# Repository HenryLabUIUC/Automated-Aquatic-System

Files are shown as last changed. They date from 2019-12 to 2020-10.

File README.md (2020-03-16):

# Automated Aquatic System
This projects includes the Arduino sketches, Fritzing diagrams, list of parts and suppliers, and various 3D printer .stl files
to build the feeding controller, and its associated peristaltic pump controller, to rear Crepidula snails and other marine
organisms. In addition, there are some dimensioned diagrams (Additional File 3) for various parts used in the automated
marine aquatic system. These files are labled and named as "Additional File #" according to the way they are referenced in
the manuscript: Henry, Lesoway and Perry, 2020, and Additional File 1, the Standard Operating Procedure (SOP) published in
BMC Biology. This project is supported by an NSF EDGE grant (no. 1827533) to J.J. Henry (J.Q.H.). See
www.life.illinois.edu/henry/tools.html

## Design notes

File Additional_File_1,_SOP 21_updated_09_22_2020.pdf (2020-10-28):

Marine Aquatic Rack System Standard Operating Procedure (SOP):

**(22 September 2020) Version 21. Henry Lab, UIUC

Jonathan J. Henry, Maryna P. Lesoway, and Kimberly J. Perry

Department of Cell & Developmental Biology University of Illinois
601 South Goodwin Ave.
Urbana, IL 61801

Note, please see the accompanying manuscript (Henry et al., 2020) and Supplemental File 2, “List of Parts and Suppliers” for more details regarding this system

This system was designed in collaboration with Iwaki Aquatics, Inc., and the automated feeding system was designed by Dr. Jonathan Henry (UIUC),
which was funded by an NSF EDGE GRANT (1827533)

Supplemental Figures are included here (called Supplemental Figures 1-4). Figure notations (to Figures 1-5) refer to those included in Henry et al. (2020). Other figure references include the corresponding Supplemental Files that accompany Henry et al. (2020), see https://github.com/HenryLabUIUC/Automated-Aquatic-System

### 1. Basic Control of the Aquatic System (Walchem Controller and Power Switches):

The main system is controlled by a Walchem 900 controller (model number WEL series 191653-20, Iwaki Aquatics, Inc., Holliston, MA; Figure 4A-B). Two electrical switches control power to the main system. A main power toggle switch (located on the bottom right of the Walchem 900 controller) will disconnect all power to the system. Note that system (e.g., main pump) power status is indicated by Alarm light A1 on the controller. A second, rotary switch (to digital input D1, on the bottom left) places the system in standby mode. In standby mode the main water pump, UV lamp, and skimmer will be turned off. In addition, the system’s electromechanical, rotary bypass valve will return to filtering mode. In standby mode all sensors will continue to operate, and the system display panel will continue to be active. Alarms may still be triggered, depending on the sensor readings. For many servicing needs, one can use the rotary standby switch to place the system in standby mode. When servicing any electrical components the system must be shut off using the main power switch and unplugged. A dedicated, 20 amp 120VAC electrical circuit is required for the operation of this system. Additional electrical circuits are needed to power other devices, such as the protein skimmer and feeding system.

Note, for specific instructions related to the use and programming of the Walchem 900 controller, readers are referred to the manufacturer’s instruction manual: https://www.walchem.com/Literature/Controllers/W900/180686_W900%20Manual_E.pdf

Some words of caution: users must be careful when accessing the system’s Walchem 900 controller to make any changes. All inputs are accepted immediately once they are entered, including any accidental changes (and no confirmation is requested when inputting changes). Any unintended changes could have a profound effect on system operation and animal welfare. At the end of this document, we include a complete list of settings used for our system.

### 2. Tools for Servicing the System (Supplemental Figure 1):

Certain basic tools are needed to service the system (Supplemental Figure 1). These include thin silicone rubber grip pads (similar to those used to open stubborn jars in the kitchen), which are handy for loosening and tightening the PVC unions. Likewise, a small filter wrench (Channellock, Inc. part no. 209, Meadville, PA) is useful for stuck PVC unions. Large and a small filter housing spanner wrenches are needed for loosening and tightening the filter bowls (Pentair parts 150296-75 and 150295-75, Pentair Aquatic Ecosystems, Apopka, FL). Two 12” standard adjustable wrenches are required for loosening and tightening various plastic pipe fittings. Basic straight and Phillips head screwdrivers for loosening and tightening clamps, etc. A specialized valve adjustment tool is needed for adjusting the tension on the large ball valves (provided by Iwaki Aquatics, Inc., Holliston, MA). In addition, an IR non-contact thermometer (e.g., EXTECH IR250, FLIR Commercial Systems, Inc., Nashua, NH) is also useful for monitoring the temperature of the main water pump housing. Handheld pH and conductivity sensors are also needed to asses water quality. The latter generally also incorporate temperature sensors as well for internal compensation. Spare fuses are needed in case the system fuse blows. Silicone grease is needed to lubricate the filter cartridge bowl O-rings. A roll of plumber’s Teflon tape is needed for sealing certain plumbing fittings. In addition, a long-handled ice scraper is useful for removing salt deposits from the system, especially those forming in less accessible areas.

### 3. The Rack Shelving Unit (Figure 1A):

The aquarium system, including the rack shelving unit was constructed by Iwaki Aquatics, Inc. (Holliston, MA). The rack is made of welded and powder-coated/painted aluminum and holds up well to salt water. Four small adjustable stainless steel feet serve to level and support the rack. As the system is very heavy once it is filled (approximately 1100 lbs/ 550 KG at capacity), these feet could eventually cause impressions in the flooring. As a precaution, and to distribute this weight, we machined a set of four ½ inch thick, 4” x 4” aluminum pads with central recesses for the leveling feet (See Figure 1A, C, and Supplemental File 3A). The typical Iwaki rack can be constructed with either five or six shelves depending on the configuration of tanks, and has a foot print of approximately 5’-6” wide x 1’-4” deep). Smaller racks with fewer shelves can also be made to order. Tall units need to be anchored either to the wall or to the ceiling to prevent them from accidentally tipping over in the event of an earthquake or if someone were to lean/pull on the unit (Figure 1A, C). There is little that needs to be done to service the shelving unit itself, other than to periodically clean it with absorbent towels and fresh water to remove spilled sea water and salts.

The main rack occupies approximately 11 sq. ft (5’-6” wide x 2” deep), which includes some space between the back side of the rack and the wall, and it is 7’-8” feet tall. For access and cleaning the rack has been placed 10 inches away from the wall. The various reservoirs, feeding system and the chiller are all external components that take up additional floor space. The feeding system (Figure 5A) occupies 3 sq. feet (1’-6” wide by 2 feet deep) and the 5 gallon sea water reservoir (a plastic bucket, see Figure 4H) requires another 1 sq. foot of space (approx. 12 inches in diameter). The external chiller occupies 1.5 sq. feet (1’ wide x 1’-6” deep). The two dosing tanks (external reservoirs) for the RODI water and a mix of calcium hydroxide, and calcium carbonate take up 1.5 and 3 sq. ft (15”x 15” and 15-½” x 21-½”, respectively, see Figure 4E).

### 4. Water Flow (Figure 2): 4.1. Water Flow During Normal Operation:

An exploded diagram has been provided to show the main parts of the aquatic system and the various routes of fluid flow (Figure 2). Note that all valves and other key components are referenced using specific numbers and initials, which we have marked with adhesive plastic labels. Relays (R#), digital inputs (D#) and alarms (A#) are numbered, accordingly, as indicated in this document. Likewise, valves are numbered for convenience, but in no particular order. Except for the needle valve #6, ball valves rotate a total of only 90° (Handle positions on ball valves relative to the long axis of the PVC pipes indicate their operation: the parallel position “|” is open; the perpendicular position “T” is closed, see examples in Figures 1L, 4N-O, Supplemental Figure 2). The ball valves typically rotate clockwise to close them and counterclockwise to open them. These directions are typically marked with arrows on the larger valve handles. Stiff, loose or leaky valves can be adjusted with a special valve adjustment tool (see below).

During normal operation the valves should be in the following positions:

1. Main pump motor inlet ball valve #4 should be completely open (Figures 1L, 2, Supplemental Figure 2A)
2. Main pump outlet ball valve #1 should be completely open (Figure 2, Supplemental Figure 2B)
3. Sensor loop ball valve #2 should be either completely open or ½ open (45° position; Figure 2, Supplemental Figure 2B)
(Note valve #2 must be completely open when using the external chiller, if it is attached to the sensor side loop.)
4. Needle valve #6 should be opened just enough to keep side bio-reactor filter loop pellets moving (Figures 2, 3L, Supplemental 2C). Turning this valve clockwise will close it. Never over-tighten this valve to completely close it, as that may damage the needle.
5. Main bypass ball valve #5 should be completely closed, unless more bypass water is required to return to the sump to prevent cavitation or to limit water flow to the tanks (Figures 2, 4N-O, Supplemental Figure 2D, see below).
6. Ball Valve #7 (“AT”) should be completely closed (Figure 2, Supplemental Figure 2E; this is the Accessory Tap Filler valve for the attached blue hose, see below).
7. Spring loaded “quick connect” drain valve #3 should be closed (Figures 2, 3L, Supplemental Figure 2C, e.g., with nothing attached!) This is the main drain valve. This male valve automatically opens when the female connector is attached, see below.
8. Individual ball valves to each row of tanks (rows lettered A-F, from top to bottom) should be adjusted as needed: typically, ½ open (45° position). If there are no tanks on these rows they should be closed (Figure 2, Supplemental Figure 2F).
9. Individual tank ball valves should be opened as needed (Figures 1D, 2, Supplemental Figure 2G). Typically, these should be completely closed if there are no tanks or open fully or less, as needed. Typically, these are set to ½ open (45°) for the 3 l tanks and both are set completely open for each of the 10 l tanks.

### 4.2. Water Flow During Feeding

(Electromechanical bypass valve, input from R3, regulated by D5; Figures 2, 5I, Supplemental Figure 2H):
Note that during feeding the filter loops (including the bioreactor side loop; Figure 2 and 3K) will be bypassed so that food can freely recirculate between the sump and the tanks. This is achieved by a motorized ball valve (Figures 2, 5I, Supplemental Figure 2H). The bypass valve is regulated by relay R3. When the relay is open, the system is in filtering mode. When the relay is closed, the system is in feeding mode. Normally, the state of relay R3 is controlled by a digital input from the feeding system (D5). A small window on the bypass valve “BP” indicates its current status (Supplemental Figure 2H). If the window is black, the unit is in filtering mode. If the window is white (side of stem colored with white paint), the unit is in feeding mode. When the valve is in the feeding position, Alarm light A3 will be illuminated. During the feeding mode, sea water will not pass through the filters due to the presence of a reverse flow check valve (Figures 2, 3L). Water flow will thus encounter less resistance due to the removal of the filters and no water will return to the sump via the small bioreactor filter loop. Therefore, during feedings the effluent, outlet pressure indicated on the round gauge will rise approximately 3psi (e.g., with a new pleated filter from approx. 10-13 PSI to 13-16 PSI; Figure 2, Supplemental Figure 2B). The flow rate to the tanks will also increase somewhat during feeding from by approximately 3 lpm (e.g., with a new pleated filter from 29-30 l/min to about 32-33 l/min, or possibly as high as 34l/min). (Note that the level of water in the sump will be lowered by about 0.5 to 1 cm during feeding). The noise level of water flowing through the main pump will generally increase during feeding. This is normal, but one should pay attention for any signs of cavitation (see below). The only bypass water that will return to the sump during feeding will come back via the sensor loop, unless the main bypass loop (valve #5, Figures 2, 4N-O, Supplemental Figure 2D) has been opened somewhat. Note that depending on the flow rate, some bypass water must return back to the sump or cavitation may occur (see below). The UV lamp will continue to operate during feeding, as it requires flowing sea water to cool it (otherwise the PVC housing would melt!; Figure 3I). During feeding the skimmer is also turned off (Figures 3C-F, 5G-H). When the filters are turned back on after feeding, there may be a slight delay in the formation of new skimmate by the protein skimmer (though we have not yet encountered any such problems). There is normally no need to make any system adjustments during feeding.

Note that as the filters become clogged, the effluent outlet water pressure will drop (as will the overall flow rate). Pressure on the intake side of the filters will increase while that on the outflow side will decrease (the latter being the pressure read by the small round gauge; Figure 2, Supplemental Figure 2B). This gauge can be used as an indicator for potential problems or when it is time to replace the pleated 50µm filter (Figure 3G, Supplemental Figure 2B), though the reading is somewhat misleading. For instance, if one opens up the valves supplying the small tanks this pressure reading will drop and the flow rate will increase. Typically, filter replacement is required when the inlet and outlet pressure difference is 10psi. Once the pressure difference gets above that, there is a small risk that the filter cartridge can collapse/crush. In our system there is no second gauge that reads inlet water pressure to the filters, so the pressure difference cannot be determined. Most labs care more about the flow rate to the tanks than the pressure in the filters. There is a direct relationship between flow and pressure with pumps, so it's easier to just change the filter according to changes in flow rate. As the filters become clogged you will also notice that the noise level of the system will become quieter, as less splashing water returns to the sump. It is recommended to change the filter once the system's filtered flow rate drops to no lower than 20 lpm, but one can change the filter before that point. One can gain some additional time before needing to perform a filter change by simply opening up the valves that supply sea water to the manifolds for each row of tanks (valves A-F). This will also impact the flow occurring during feedings, which will also be elevated (one should limit the maximum flow during feeding to around 35-36 lpm). At some point though, the effluent water pressure will drop to low and the float switch will not rise, triggering a no-flow alarm. At that point the filter must be changed immediately, as this will begin to impact the reading of temperature, conductivity and pH, which may lead to lethal changes, as the system tries to compensate for the false readings! While in some other applications it may be possible to clean clogged filters, in our case the biofilm, finer debris and algae trapped by the filter material are much harder to remove simply by washing the filter, and, thus, the filters must be replaced. Furthermore, the material that is trapped by the filter will continue to break down within the system, so the longer the waste/food stays in the system, the more organics/nitrogenous waste will accumulate in the water. Filtering flow rates with new filters are around 29-30 lpm, and effluent pressures should return to around 10-12psi (32-34 LPM and 13-15psi during feeding). We have observed approximately two—three months of service life for each pleated filter.

### 5. Individual Tanks (Figures 1D, 2):

The polycarbonate tanks are manufactured by Pentair Aquatic Ecosystems (Apopka, FL; Figure 1D-G). These tanks accept slotted or nylon mesh “larval” baffles (Figure 1F). The larval baffles are available in three mesh sizes (400, 700 and 1000µm). These baffles slide into molded channels in the back of each tank and are fairly secure. Their purpose is to prevent animals from reaching the rear drain tube where they could travel to other parts of the system. In this system we use baffles with 400µm openings, which are small enough to prevent Crepidula atrasolea embryos or juvenile snails from escaping the tanks. Each tank is equipped with a plastic lid (Figure 1E). Unused holes in these lids are plugged with small white plastic snap caps to help limit evaporation and water spray (Figure 1G; McMaster Carr, part number 9688K25162PP050BG14, Elmhurst, IL). These plugs can be further sealed using silicone aquarium cement (Supplemental Figure 2G).

1. NOTE: When servicing a tank, first shut off the tank’s own valve(s)! Then remove the white tubing from the lid access hole(s) before removing the lid or the tank. Be aware that there may be a lot of moisture (typically fresh water condensate) under the lids. When removing a lid, be careful to drain this condensation back into the tank to prevent a mess.
2. If the tank is to be removed, tilt the tank backwards to drain off some sea water first. Remove the tank carefully so as not to spill the sea water. Lift the tanks straight up to clear the drain tube from the drain cover (Figure 1H-J), and the ridges on the bottom of the tank, which straddle the rack cross bars (Figure 1E, G). When done, reinstall tank and/or lid in reverse order, insert the tubing and then turn the tank valve(s) back on. It’s easy to forget this last step. Remember to seat the tanks properly, as they have protruding plastic ridges on the bottom that must seat properly onto the metal rack cross bars (Figure 1A-D).

One can operate the system with any number of tanks in service. However, when taking tanks on or off line, they should be added or removed with sea water in them. Otherwise, the sea water level in the sump will change.

The mesh on the larval baffles will eventually accumulate a biofilm and waste products, which will impede the flow of drain water. This could lead to an overflowing of sea water from the tank, which could eventually drain the sump. These larval baffles must be cleaned periodically, and it is best to do this on a predefined schedule (every month or two).

Note that if the flow of water through any of the small valves that serve individual tanks becomes reduced, this may be an indication that they have become clogged. Opening and closing the valve may correct the problem, or one can try to unclog these valves by temporarily shutting off all the rest of the small valves that serve other tanks on that particular shelf. The greater force of the higher water pressure will usually dislodge any debris and restore normal water flow thru the clogged valve. If this does not correct the problem, it will be necessary to remove (unscrew) the valve from the manifold to manually clean or replace it.

### 6. RO and pH Reservoirs (Figures 1A, 2, 4E):

(pH pump currently not in use)
Two plastic reservoirs with lids hold RO (RODI) water and a concentrated salt solution, respectively (Figures 1A, 2, 4E). Be sure to periodically check the levels and refill the RO (dH2O) water and pH salt reservoirs, as needed. Make sure the reservoir lids are correctly installed and the filler intake/vent tubes are in place! The filler tube has a cylindrical weight to keep it submerged. For the pH reservoir one can mix dH2O with Na-bicarbonate (dissolved to about one half of its saturation point, or 40gm/liter) and Kalkwasser (Ca-hydroxide, dissolved to about half its saturation point, Bulk Reef Supply, Golden Valley, MN). Note, however, that we have not been using the pH pump, and have inactivated this by placing it in HOA off mode (see additional note, below). Rather, we adjust pH manually, as needed. On rare occasions, during the initial establishment of this system, the pH dropped by 0.1 unit. To correct this we added 5gm of Marine Buffer (Seachem, Madison, GA) per 40 gallons of sea water. This elevated the pH by 0.1 unit. More recently, we saw a slight elevation of pH. To correct this issue, we performed a series of partial water changes and began to supplement ionic calcium (see Section 11: Monitoring Water Quality, and Section 45: Elevated pH, below).

### 7. Adjustment and Priming of the RO (input from R4) and pH (input from R5) Pumps (Figures

2, 4F):
RO and pH pump operation are indicated by Alarm lights A4 and A5, respectively. Normally, these small red and blue electromagnetic relay pumps, mounted on the back wall to the right side of our rack system, make a distinct rhythmic sound during pumping (Figure 4F). When the pumps are running dry and pumping air they will make a much louder popping sound. This is not good for the pumps and is caused by fluid level in the reservoirs being located below the weighted inlets of the supply/vent tubing, or the pump(s) may need to be re-primed. Priming is accomplished by opening the small round plastic valves on the very top of the pumps (Figure 4F, see the manufacturer’s instruction manual). Make sure there is enough liquid in the reservoirs. Allow the pumps to run by placing them in HOA “On” mode using the main system control panel. The pumps are primed when fluid starts to exit the vent tubes that hang back down into the reservoirs. At this point the small valves should be closed to allow the fluid to pump to the sump instead. Be sure to verify that this is working! After the problem is corrected return the pump control to HOA “Auto” mode using the main system control panel. RO pumping rate is set to 40 pulses per min. This must be set on the front panel of the RO and pH pumps themselves (Figure 4F; follow the manufacturer’s instructions, Iwaki Co. Ltd., Holliston, MA). Adjustments can only be made in the upward direction, so if you miss your desired setting you must go all the way up and back to zero to reset the proper value. These values are typically set to be “locked” on the RO and pH pump control faces so that one cannot accidentally change these (users are referred to the pump manufacturer’s manual for full operation). Pumping rates may be changed, if needed. For example, if the restored levels tend overshoot those desired, then the pumping rate can be lowered (e.g., conductivity overshoots and goes too low, triggering an alarm, during RO water pumping). With lower pumping rates the pump will tend to run longer but the water will have a better chance of mixing so values will be able to stabilize , which helps limit false readings made by the sensors.

**So far, we have not seen any need for the pH dosing pump. pH levels appear to be holding fairly steady; though earlier we had noticed these values slowly drop once we added animals and began to feed them, and more recently (after eight months of operation) we saw a slight elevation in pH (see Section 11: Monitoring Water Quality). We are considering a change to the use the pH pump to deliver periodic, scheduled doses of Ca++ to the system to enhance shell growth.

### 8. Servicing the Sump Pad Filter (Figures 2, 3A):

The sump has a coarse, fibrous polyester filter pad that sits on a perforated sieve plate (Figure 3A). Dirty sump pad filters may be carefully removed allowing any sea water to drain back into the sump and replaced with a fresh filter, as needed. To accomplish this, one must remove the Tent or Origami cover (Figure 3B, Supplemental Figure 3A-C). It is not necessary to remove the slotted PVC drain diverter or to shut the system down to change the filter pad. Change the filter when it becomes discolored and sea water starts to spill over the edges rather than pass thru the filter material. These disposable filter pads should last a few months.

### 9. Servicing the Protein Skimmer (regulated by D5, input from R7, Figure 3C):

The sump contains a compact Tunze protein skimmer (Tunze Comline DOC Skimmer, 9004 DC, Penzberg, Germany) that fits inside the left compartment of the sump on the far left side (Figures 2, 3C-F). Protein skimmer status is indicated by Alarm light A7. It is illuminated whenever the skimmer is turned off, which occurs during a feeding cycle. The protein skimmer is located in the sump and runs automatically when the filters are active, but is turned off during feeding via a custom microcontroller circuit (Figure 5G-H; see Supplemental Files 15-18). Normally, a low level output (0) from pin 3 of the Tunze motor controller’s ATMEL 1724 microcontroller turns on the 12 volt DC motor, and a high level output (1) stops the motor. This is the output that is being intercepted by the accessory microcontroller interface, under control of a signal sent by the Walchem 900 controller, when it receives the over-riding command from the feeding station’s microcontroller. In other words, when it is time for feeding, the feeding station sends a signal to the Walchem 900 controller to activate the bypass valve (see below). The Walchem 900 controller then sends a signal to the accessory skimmer control circuit which, in turn, interrupts the output of the DC motor controller’s own microcontroller to turn off the skimmer. Note that the blue skimmer control power light (located inside the skimmer control box knob) will stay illuminated even during feeding (Figure 5G). One can override skimmer function and turn off the skimmer at any time for a preset period (approx. 10 mins) by pushing the small button on the small skimmer control box (Figure 5G, the blue light will then go off). The skimmer can be turned back on by pushing the button again or it will automatically turn on after the preset time interval. The speed of the skimmer DC motor is regulated by the illuminated knob on the control box (Figure 5G). Typically, this only needs to be set to the 30-50% position, as needed. If this is adjusted too high, excess sea water will enter the skimmer cup. If this is set too low, no skimmate will be formed. This needs to be adjusted empirically. Skimmate needs to be removed from the collection cup (Figure 3D-G), and its rate of formation depends on several factors, including the size and amount of bubbles and the concentration of dissolved organics. As supplied, the removable Tunze skimmer collecting cup does not have a drain tube. We have installed a silicone drain tube that exits the sump on the left side through a bulkhead compression fitting located just above the high water line on the far left side of the sump (Figure 3D, F; silicone tubing: 0.188” ID x 0.375” OD, Dow Corning, Midland, MI). Be careful with the skimmer’s silicone drain tube. If it becomes disconnected from the small collecting cup the skimmate will simply flow back into the sump. If it gets kinked and collapses inside the sump bulkhead connector, a leak may form. This tubing can be fed to an external tray to collect the skimmate (Figure 3G). Note, however, that sea water can enter the collecting cup, as described above (and also see note below), and this would drain out of the tubing to the bucket. A great deal of water could flow through this tubing, which is located just at or slightly below the high-water level in the sump! This could create a huge mess, though we have never encountered such a problem. Alternatively, the open end of the tubing can be elevated well above the water level in the sump and lowered to drain the skimmer cup, as needed. Periodically (once every week or so) one should wipe clean the inside of the skimmer collection cup, its airlift (chimney) and the lid, which will accumulate a great deal of algae and other proteins. More skimmate will form if one keeps the chimney clean (Figure 3E). The skimmer is normally controlled by relay (R7). When relay R7 output is low/off (0) the skimmer will run and when relay R7 is high/on (1) the skimmer will stop.

Note that the skimmer is held in place by two strong rare earth magnets (Figure 3D) enclosed within the blue and black plastic disks located on the outside, left side of the sump. Do not remove these magnets or attempt to reposition the skimmer. (Also, never put the two magnets together as you will not be able to separate them without tremendous difficulty!). The skimmer sits on top of a perforated platform inside the sump. The platform has four leveling, height adjustable legs. These are set so that the slotted openings in the skimmer cup are located just along the sump high water level (Figure 3C). Sea water must be able to enter these slots. The relative water level in the sump is critical for proper function of the skimmer. It should be about halfway up between the top and bottom edges of the intake slots located within the skimmer cup. If the water level is too low, or the skimmer is placed too high, no skimmate will form. If the water level is too high, or the skimmer is placed to low, the skimmer will pump excess water into the collection cup and its drain tube. Precise sump water level is maintained by the RODI pump and the ATO units (see Section 6: RO and pH Reservoirs, above, and Section 33: Automatic sea water Top-Off system (ATO), below). Note that skimmer activity and the Walchem 900 front panel alarm light A7 are regulated by the input from the feeding system (to D5).

Note that the fine bubbles produced by the protein skimmer can also produce jet drops and a fine mist that collects under the lid and this moisture drips into the collection cup. This can fill the cup prematurely, and removes some “clean” system sea water. Careful adjustment of the DC motor’s speed can help limit this mist and any lost sea water. Approximately 25-100 ml of liquid waste will be collected by the skimmer each day.

Note also that if you perform a partial sea water change, you may see some excess water being ejected into the skimmer cup, which may flood the collecting tray. This can continue for a couple of days, and it is best to monitor this. It is unclear why this happens, as the level of sea water in the sump is not changed. One can simply turn down the skimmer settings, or elevate the skimmer drain tube to prevent the loss of sea water from the system while this is taking place.

### 10. Servicing the Cartridge Filters, General Instructions (Figures 2, 3G, K) :

The system has four cartridge filters (see Figure 2): 1) a 50µm pleated filter (Figure 3G, Supplemental Figure 3D), 2) a biological filter (Figure 3G), 3) an activated carbon filter (Figure 3G), and 4) a small nitrate bio-pellet reactor (Figure 3K).

1. When servicing the cartridge filters, put the system in standby mode, or shut off the system. The main pump must be shut off. Wait for about one minute for all the sea water to drain back to the sump, once the system is placed in standby. Service each filter, one at a time, as needed.
2. Close valves #4, 1, 2, 6 and 5.
3. Drain sea water using valve #3 with a push-on, female quick connector and its short piece of tubing. (Use a large clean beaker to collect the sea water, which will be returned to the system.)
4. Also purge some air and additional sea water (via valve #3) from each filter by pushing the purge valves on the top back sides of the filter housings (Supplemental Figure 3E).
5. Remove the stretchy nylon opaque sleeve, and use filter wrenches to loosen the filter bowl over a 3-5 gallon bucket to catch the sea water (Supplemental Figure 3D-F).
6. Once loosened, use both hands to completely remove the filter bowls with their contents. Note that the filter bowls are full of sea water and media, and are very heavy. Do not let them fall and crack.
7. Be sure to reassemble filters correctly with the appropriate cartridges, gaskets, etc. and in the correct orientations. A little 95% pure (Danco #88693, Irving, TX) silicone grease may be used on the filter bowl O-rings and threads.
8. Filter bowls should only be tightened by hand. You may use the filter wrenches only sparingly. Do not overtighten the filter bowls, you can crack the plastic or seize the threads!
9. Return the valves back to their original open states.
10. Turn the system back on.
11. Return the collected, drained sea water back to the sump. As you will tend to lose some sea water, the sump level will be low and you will likely need to add additional sea water to the system to return the level back to normal. This can be done by simply turning on the ATO unit briefly, see Section 33: Automatic sea water Top-Off system (ATO), below.

### 10.1. Servicing the Pleated Mechanical Filter (Figures 2, 3G):

The 50µm pleated filter (Supplemental Figure 3D; GPE50 Keystone Giant Filter Cartridges, CECO, Telford, PA) should be changed when it becomes discolored and begins to impede sea water flow (reducing the flow rate to nearly 20 lpm, see above). These polyester filters are easy to install and have no polarity. The pleated filters typically have a life span of a few months. Note that when the pleated filter is changed, the system’s effluent pressure and flow rate should rise. The increased flow rate will tend to drop the water level in the sump, somewhat. Therefore, some additional sea water may need to be added to the system to raise the water to its nominal level. The automatic top off unit (ATK) would also raise this level the next time (day) this unit will run. It is recommended to cover the filter bowl with dark, opaque material to discourage algal growth on this filter (Figure 3H).

### 10.2. Servicing the Biological Filter (Figures 2, 3G):

The main biological filter consists of a mix of 800 gm of Matrix (Seachem, Madison, GA) and 100 gm of de*Nitrate (Seachem, Madison, GA, see Figure 3G). This highly porous media serves as a substrate for aerobic and anerobic bacteria to process ammonia, nitrite and nitrate. This quantity of media has over 1400 sq. meters of surface area to support bacterial growth. The inclusion of some de*Nitrate granules in the biofilter also helps to remove nitrates. Note that there is a small 3” diameter sponge-like filter inside the biological filter canister to help retain the pellets. The biological filter media should never need to be replaced. Typically this filter requires no servicing; however, it can be rinsed while still inside the cartridge using clean sea water and a 5 gallon bucket, if needed, to remove any debris. Never rinse this filter with fresh water as this would harm the bacteria! It is recommended to cover the filter bowl with dark, opaque material to discourage algal growth on the filter (Figure 3H).

### 10.3. Servicing the Activated Carbon Filter (Figures 2, 3G):

The activated carbon filter contains approximately 1-2 lbs of activated carbon pellets (Figure 3G; Kent Reef Carbon Pellets, Kent Marine, Franklin, WI). Activated carbon is a porous substance with a very high capacity for absorbing organic materials. The carbon pellets can also serve as a substrate for nitrifying bacteria. The activated carbon (Kent Reef Carbon, Kent Marine, Franklin, WI) should be replaced, as needed. This filter cartridge holds a considerable amount of activated carbon (about two pounds) and should last for a year or more. This is far more carbon than is needed and some recommend using far less or even no carbon at all. Unfortunately, there is no good way to tell when this filter is depleted. If the sea water should turn yellow, it might be time to change the activated carbon. Note that there is a small 3” diameter sponge-like filter inside the activated carbon canister to help retain the pellets, and this should be rinsed and reused if the media is changed. We recommend changing the activated carbon every one to three years. Only half of the carbon should be changed. When replacing the activated carbon, one needs to thoroughly rinse the new carbon in dH2O to remove fine particulates. A mesh bag is provided for this purpose; however, one can also rinse the carbon directly in the cartridge using a large plastic bucket (only if all the carbon is being changed). One concern is that the activated carbon may impact the pH of the system. This issue seems to depend on the source of the carbon. One should monitor this carefully. Activated carbon may also remove certain trace elements from the sea water. Commercial preparations may be used to add back trace elements. If used, they should be added when the filters are in bypass (feeding) mode. Activated carbon may also release phosphates into the sea water, which is not desired. The activated carbon also acts as an additional biological filter, providing substrate for bacteria. One should cover the filter bowl with dark, opaque material to discourage algal growth on the filter (Figure 3G).

### 10.4. Servicing the Nitrate Bio-Reactor (Figures 2, 3K):

A small bio-reactor side loop filter (nitrate bio-reactor) has been included to encourage the growth of denitrifying bacteria (e.g., both aerobes and anaerobes, etc.) to help remove nitrogen (nitrates; see Figure 3K). A relatively small amount of water is slowly diverted to this side loop via the needle valve (#6; Figures 2, 3L, Supplemental Figure 2C). Needle valve #6 should be opened enough to keep side filter loop PHA pellets moving gently. (Turning this valve clockwise will close it). Never over-tighten this valve as that may damage the needle. The PHA pellets (Vertex Aquaristik Pro-Bio Pellets, Huntington Beach, CA) must be kept moving to dislodge the accumulating bacterial byproducts in which the nitrogen is being sequestered, and to prevent the pellets from sticking together. These PHA pellets contain a source of carbon needed by the bacteria to remove the nitrates. It is best to keep the bio-reactor in a dark area away from light to prevent algal growth (we cover this canister with dark, opaque material). These nitrogen rich by-products need to be removed from the water using the protein skimmer. Ideally, the water from the side loop should be returned directly back to the sump, near to the protein skimmer’s intake. To service the bio-reactor, place the system into standby mode or shut off the flow of water to the side loop (close valve #6).

If the flow of water is too slow or if a large amount of bacterial film and their by-products begin to accumulate, the pellets my stick together and stop moving. One can place a small 1/2” long yellow Teflon coated magnet (i.e., stir bar) inside the bio-reactor filter cartridge along with the PHA pellets. One can then use another strong rare-earth magnet, which is held externally by the hand, to move this stir bar and dislodge any stuck pellets without having to shut off water flow or open the filter. Alternatively, if the pellets refuse to move one should open the filter. To accomplish this, shut off water flow to the side reactor (Valve #6), bleed in some air by pushing the purge valve located on top of the filter holder, and then remove the filter bowl. As long as valve #6 is fully closed, it should not be necessary to shut off the main pump, or place the system into standby mode, to perform this service (One should verify that no water is returning back to the sump via the return hose connected to this filter, though it is perhaps safer to place the system in standby mode). Note that if the pump is running, some signs of cavitation may be detected. In that case, simply open up the main bypass loop just a little bit until cavitation stops (Valve #5). Note that the bio-reactor is located in a rather confined space next to the main pump, so be careful not to spill sea water when removing the cartridge bowl. Once the bowl has been unscrewed, it must be tilted to remove it; therefore, some water should first be removed using a large pipette to prevent spilling. Be careful, the main pump motor with its electrical connection is located adjacent to the bioreactor! Once enough water has been removed you can carefully tilt and lift out the filter bowl without spilling the remaining sea water. (By following this procedure, one should not have to remove the carbon filter to remove the bioreactor filter.) Once the bowl is removed, you will notice that the inner cartridge has a round cap and a slotted filter screen to prevent debris and pellets from leaving the filter, and these must be cleaned. Make note of their correct orientation for proper reassembly. Pull out the cartridge slowly and then slowly poor off some sea water remaining in the bowl and save this. The cartridge can then be placed back in the bowl, and vigorously moved repeatedly up and down inside the sea water remaining in the filter bowl to dislodge the bacterial film. One can also use the long plastic pipette to vigorously stir the pellets. Remove the inner cartridge from the bowl with the pellets and discard the dirty sea water left in the filter bowl. Repeat this wash one more time with some more of the clean sea water. Only clean the little round slotted screen in the sink using distilled water and wipe clean using paper towels. Do not rinse the cartridge, bowl or pellets with anything other than sea water, so as not to destroy the bacteria! Reassemble the various part of the filter in the reverse order and screw the bowl back in place. Once the filter is replaced, restore water flow to the bio-reactor side loop (open valve #6 just enough to get the pellets moving). If they are not cleaned sufficiently, fragments of biofilm may continue to come off the pellets and be drawn into the slotted plastic filter screen, which could impede water flow, and this would need to be re-cleaned. Note, to get all the flowing sea water back into the bio-reactor’s filter bowl, the purge valve needs to be pressed to remove the air (you may hear a little hiss as the air escapes). Stop pressing this button once all the air is gone and a little water starts to leak out of the purge valve. Be sure to return the main bypass valve #5 back to its previous setting when done servicing the bio-reactor. Some additional sea water will need to be added back to the system to replace that discarded during cleaning. It is a good practice to keep an eye on the bio-reactor and to periodically dislodge or clean these pellets.

The consumable PHA media in the small side loop filter should be replenished, as needed, when it is consumed (this typically has a very long lifespan equal to several months). Only about ¾ inch depth of fresh static media should be placed in the small side loop filter bowl (Figure 3K). The volume of the fresh, slowly tumbling consumable media will appear to be about 1 inch deep when the sea water is flowing. One must to be careful to keep these pellets moving, and not to add too great or too small a quantity of these pellets. It is far worse to add too much than too little. Too much PHA media, too little water flow (impeded movement of the pellets) or insufficient levels of oxygenation can create toxic levels of hydrogen sulfide. We have found that these pellets are reduced to approximately half their diameter after about 3-4 months of use. At that point some additional fresh pellets need to be added. When adding new pellets, do not discard the old pellets, which have the necessary bacteria growing on their surfaces.

### 11. Monitoring Water Quality:

Users are required to check the health of the biofilters by measuring the levels of ammonia, nitrites and nitrates on a regular (weekly) basis. We also measure levels of phosphate, general water hardness (KH), calcium, and pH regularly. Kits are also available to measure various specific water quality parameters. To monitor these levels we use test kits produced by API Marine (Mars Fishcare North America, Chalfont, PA), following the manufacturer’s instructions. Kits and instruments are available from many other manufacturers, but we find these kits to be good compromise between cost, ease of use, and accuracy.

For animals that secrete calcareous elements (e.g., gastropods, urchins, corals), calcium levels should be maintained at high levels (~400ppt). In our previous system (Henry et al. 2017), a large bed of crushed coral provided useable calcium (measured at 380-420ppm), in addition to buffering capacity to maintain pH levels. In the recirculating system, the combination of reduced volume of crushed coral (Figure 4M) and a rapidly growing snail population reduced calcium levels, in turn increasing water hardness (KH) and pH. To address immediate concerns (after 8 months in service), we performed a series of partial water changes (maximum 20% of water volume at one time). Over the longer term, we have initiated the use of an ionic calcium supplement, to increase calcium levels without affecting pH or carbonate levels. We use Reef Advantage Calcium (Seachem Laboratories, Madison, GA) to maintain calcium levels at 380-420 ppm and balance water hardness and pH, following the manufacturer’s recommendations. Calcium chloride should be added slowly to the system, per the manufacturer’s instructions, as excess doses can affect carbonate alkalinity and pH. Once calcium levels are stable, the user can determine how much supplemental calcium should be regularly added to the system, which will vary depending on population size and growth rates.

Many aquarium users add kalkwasser as a source of calcium, however, this can impact alkalinity (KH) and pH, and can be more challenging to dose. Water quality parameters should be checked regularly (weekly), and additional calcium added as required. For urgent situations, water changes (no more than 20% of the total volume at a time) can also be implemented. A calcium reactor may also be added to the system to automatically regulate calcium, alkalinity, and pH in the system.

Measures may also need to be taken to regulate the level of phosphates (see Section 44: Phosphate levels).

### 12. Servicing the UV Lamp and Quartz Sleeve (input from R2, Figures 2, 3I):

(Currently not in use)
The UV lamps consists of a 57 watt Aqua Ultraviolet lamp (Figure 3I; part number A20057, Aqua Ultraviolet, Temecula, CA) contained inside a 19” long Classic quartz sleeve (part number A10057, Aqua Ultraviolet, Temecula, CA), which is located inside the plastic housing (Figure 3I). Power to the UV lamp is controlled by relay (R2).

Turn Off the system to avoid electrical shock!
The UV light helps sanitize the water by killing circulating microorganisms. The sanitizing efficiency of UV light is related to UV intensity and water flow rate (e.g., UV exposure amount/time). UV output diminishes with use, and therefore, the UV bulb has a limited lifespan and should be replaced once each year. In addition, the quartz sleeve that protects the UV bulb must also be inspected and cleaned if deposits have formed, whenever the bulb is changed. UV operating status is indicated by Alarm light A2. UV bulb illumination can also be verified by the presence of a pink/blue light seen through the transparent blue plastic bell located at the top of the bulb housing (Figure 3I). The UV bulb is 57 watts and is designed to have a 95% efficiency at the end of its 1 year rated lifespan (9000hrs; equal to 110µW/cm2). At that time the quartz sleeve should also be inspected and cleaned, as needed. These parts are to be removed separately, starting with the UV bulb. First the system should be turned off and unplugged. The water should be allowed to drain back to the sump and main outlet valve #1 and sensor loop valve #2 should be closed (Figure 2, Supplemental Figure 2B). The UV bulb may be removed alone without opening up the quartz sleeve sea water compartment by loosening the black nut

located just above transparent blue plastic bell (Figure 3I). Only handle the UV lamp and quartz sleeve with clean gloves. Once loose, the bulb will slide straight up out of the holder along with its electrical connections. After the UV bulb is removed one can also remove the quartz sleeve by loosening the transparent plastic blue bell (Figure 3I). Once loose, the sleeve, which looks like a giant test tube, will slide straight up out of the holder. Note that unlike the UV bulb, the outer surface of the quartz sleeve is exposed directly to the sea water. The quartz sleeve may be dried and wiped clean using cotton wipes or cheese cloth. If scaled, some mild vinegar may be used to dissolve the calcium deposits located on the outside of the sleeve only! Rinse the outside with distilled water when done. Do not let any liquid enter the quartz sleeve or contact the UV bulb or its electrical connections! They must remain completely dry. The bulb and sleeve are very fragile. Great care must be taken so that they are not scratched or broken. The bottom, closed end of the quartz sleeve is particularly fragile. Reassemble these parts in the reverse order, making sure that the fittings have been tightened to prevent leaks.

The UV bulb must be cooled by running sea water, otherwise the schedule 40 PVC black plastic housing will melt. Do not operate the UV lamp, if there is no running sea water! The UV ballast, which is contained in its own separate plastic housing, should last for several years (Figure 3J). When it fails it typically shorts closed and the circuit’s fuse will blow. Note that the same fuse also supplies power to the main pump motor, so the water pump will also stop, triggering a no/low flow condition that will shut down the system.

** The UV lamp provides for a very aseptic supply of water to the tanks. This may limit the number of beneficial bacteria in the system but it should help limit the spread harmful microbes or other planktonic organisms. In the past, we have never needed to worry about problems with such contamination when using simple 30 gallon aquaria. Hence, it may prove that we do not require the UV lamp. Use of natural sea water, operation of the system near natural marine sources of contamination, or culture of more sensitive organisms may necessitate use of the UV lamp. So far, we have never turned on the UV lamp. Any effect of the UV irradiation on the phytoplankton food added to the system, is undetermined.

13. Aquarium System Temperature Regulation (heater regulated by S14, input from R6, Figures 2, 3E):
A titanium heater (Finnex TH500-X, 500 watts, Chicago, IL) is located on the floor of the left sump compartment, just below the protein skimmer (Figure 3E). Heater status is indicated by Alarm light A6 (active when illuminated). As supplied, our aquarium system has no active cooling, and the only controlled input is from this heater, which can only be used to raise the water temperature. (However, see additional external chiller, below). The activity of the heater (R6) is regulated by readings on the temperature probe located within the pH probe (S14). (Alternatively, it can be set to be regulated by the temperature probe located within the conductivity sensor (S13)). In addition, the main pump and the UV lamp provide a constant source of heat. To some extent, aquarium system temperature is related to room temperature. As room temperature rises, so can the water temperature. Room temperatures must, therefore, be kept low for maintaining tropical animals. Ideally, the room temperature should be 18-22°C. While the inclusion of covers on the tanks and the sump will limit evaporation, they will also trap heat and limit the rate of cooling. Therefore, without a chiller, or a cold room temperature, it is not possible to completely seal the aquarium system from evaporation, as it will begin to overheat. Ideally, aquarium water temperature should be maintained at 27°C for Crepidula atrasolea snails. Note that the readings on the main system controller may not accurately reflect those inside the individual tanks. Temperatures should be verified using a reliable thermometer. Snails can tolerate a temperature range of 23-29°C, but the extreme temperatures put a great deal of stress on the animals and will kill them. Alternatively, one can use a small aquarium chiller to lower temperatures, as needed (see below).

If the room temperature is going to get too hot (e.g., hot summer months, failure of building air conditioners, etc.), it will be necessary to install a water chiller. The best configuration is to have the chiller installed during production, with the chiller loop located directly inside the sump and regulated by a common temperature control circuit used for the heater. Alternatively, one can tap off of the system to divert some pressurized water to a small chiller, as described below (Figures 2, 4C, K-L; Supplemental Figure 2B). Please note that chillers will also generate their own heat, which can elevate room temperature even further. The water chiller does not need to be used at all times (see below), but is a permanent installation to the system. Chillers require a specified flow of sea water typically of at least 3 gallons/min. The chiller must also be rated to handle at least 25 PSI of inlet water pressure, which is the maximum rated output pressure of the water pump, though in practice water pressure to the chiller will be much lower. One may need to use a pressure regulator to lower the input pressure to the chiller, and reduce the flow rate to one specified for the chiller. As we supply water to an external chiller via the sensor side loop, there is little concern, as pressures there are much lower. Input water to the chiller can also come from the Acc. Tap filler hose (Figure 2, Supplemental Figure 2E), which can deliver greater pressures and flow rates (controlled by valve 7). The chilled water needs to be returned directly back to the sump (Figures 2, 4N), and those lines should be enclosed with foam insulated tubing secured with zip ties (Figure 4K-L).

### 14. External Chiller System (Figures 2, 4K):

An external 1/10 hp titanium chiller (JBJ Arctica DBA 075, JBJ Aquarium, Inglewood, CA; Figures 2, 4K) has been installed to lower sea water temperatures, as needed. The chiller is a simple flow-thru system and does not have an internal pump. Therefore, one must feed the chiller with pressured water from the rack system. To accomplish this, the chiller receives the effluent sea water from the sensor side loop (Figures 2, 4C, K-L; see Supplemental File 3E), which ranges between 10-14 psi or lower as the pleated filters become clogged. Note that this particular chiller does not require a pressure regulator, as the pressures are below the
maximum rated safe pressures. The chilled water is returned directly back to the sump using the side loop’s final effluent tubing connection located directly in the sump cover (Figures 2, 4N). The chiller will maintain cold water temperatures to within 1°F of its set point. Note that unlike the rack system, the chiller readings/settings are in °F. It is important to set the chiller to a temperature above that normally desired for the system (i.e., the heater temperature setting), so that the chiller and heater do not end up competing against one another. For example, if the desired system (heater) temperature is set to 27°C (80°F), then the chiller should be set to 28-29°C (82-83°F). This ensures that it only turns on when the sea water temperature well exceeds that of the desired heater temperature, and does not chill the water below that of the normally desired heater water temperature (which would in turn re-activate the heater, ad infinitum). The actual setting of the chiller must be determined empirically. We have the chiller set to 82°F which will be activated at that temperature and will turn off once the water reaches 81°F. For accuracy, the chiller’s displayed temperature reading must initially be calibrated, as described by the manufacturer (Figure 4K). The chiller is essentially a permanent installation and can be left on at all times. It will only be activated when the water temperature rises above the chiller’s set point. Alternatively, the chiller power can be turned off (un-plugged), if warm room/water temperatures are not expected. Sea water will simply flow unimpeded through the chiller’s plumbing system. The chiller water flow and hose connections should be inspected periodically and back-flushed, as recommended by the manufacturer.

Note, that the addition of the chiller reduces the flow of water through the sensor side loop. Currently, with the chiller installed, far less than ten gallons per minute flow through the chiller and side loop when in feeding mode (and even less when in filtering mode). The chiller actually specifies a 960 liters per hour, maximum flow rate (16 liters per min). While system flow rates range from 20-33 liters per minute (depending on the mode and condition of the filters), the flow through the sensor side loop is much less and will not exceed the chiller’s specifications. If the flow rate is too slow, however, it could cause the sea water to freeze, blocking flow to the chiller and sensor side loop (sensed by the float switch; Figures 2, 4C), which would activate a system alarm. The chiller has built in protection to sense when the coils become too cold, which will shut down the chiller (but not the aquarium system). As a safety precaution, the sensor side loop float switch could be wired to control power to the chiller, such that if water flow is interrupted, the chiller could be powered down using an accessory circuit. There is an unused relay within the Walchem 900 controller that can be used for this purpose (R8). Note that if water flow is interrupted to the sensor side loop, those sensor readings will begin to change dramatically. This will have an impact on the regulation of temperature, conductivity and pH, which could harm the animals. Alternatively, one could add the appropriate fittings to supply water to the chiller by using the accessory filler tap (valve # 7; Figure 2, Supplemental Figure 2E); however, this would rob the tanks of some water flow. In this case one would also need to install a new drain port in the top of the sump cover to return the chilled water back to the sump.

Never tilt or turn the chiller (compressor) onto its side. If the chiller is moved or tipped over, it should be left standing upright for at least 4 hours until the power is restored, to allow the oil to return back to the compressor.

Note that we encountered an issue related to decreased flow through the sensor loop with the addition of the chiller. This tended to reduce water flow to the point where the float switch would send a premature warning of a no (low) flow condition. To correct this we substituted the 3/8” inch OD effluent tubing attached to the chiller with 1/2” OD tubing, which increase the water flow.

### 15. Servicing the Sensors (recalibration, Figure 4C, Supplemental Figure 4):

When servicing the sensors (e.g., for cleaning or recalibration) in the side loop, one can simply shut off the sensor side loop ball valve (#2) by turning it clockwise 90 degrees, see Supplemental Figure 4A. (Be sure to Disconnect power to the chiller first, as one should never let the chiller run without flowing sea water). Shutting off the side loop water flow alone will not place the system in a standby mode, as the main pump will continue to run, but the flow switch (D3) will immediately register a “No flow” alarm. Pressure on the effluent water gauge will rise 2-3 psi. Alternatively, one can put the system in standby mode, which will shut down all water flow, and both the flow sensor (D3) and the paddle wheel flow sensor will immediately register “No Flow” alarms. Note that during re-calibration, various alarms may be thrown, as the sensors in the side loop will respond to changes in water conditions. This is due to the fact that when water flow is shut off to the sensor loop, the readings for temperature will begin to fluctuate and those for conductivity and pH will tend to drop over time. In addition, when the system is placed in standby mode the water level in the sump will rise by a few cm, as water drains back from the tanks, which may trigger a high water level alarm. However, while performing the actual sensor calibrations when inside the Walchem 900 controller’s menu driven system, alarms and any automatic adjustments of water conditions will be temporarily suspended. Afterwards, be sure to restore flow to the side loop gradually by slowly turning back on valve (#2). If the flow switch does not rise back upwards to signify flow, the no flow alarm will remain active. In that case, one can simply turn of the valve (#2) and turn it back on more quickly. As long as the flow switch is lifted, the sensor loop is getting enough water flow. (In addition, be sure to Restore power to the chiller).

As noted above, sensor readings can change with changes in flow rate and will drift in static water when water flow is interrupted to the sensor side loop or the system is placed in standby mode. It may take some time for these readings to stabilize and return to normal after water flow is restored (one to two days), so one should monitor the system very closely until they are stable. It may be necessary to temporarily place the RO and pH pumps in HOA OFF mode, until the readings have stabilized so that they do not change the desired parameters (see below).

15.1. Calibration of the pH probe (output to S13, Walchem 191653-20, Figure 4C, Supplemental Figure 4B-D):
The system is equipped with a Walchem pH sensor (Figures 2, 3C; Supplemental Figure 4B; model number WEL series 191653-20, Iwaki Aquatics, Holliston, MA). The pH probe must be calibrated periodically, as needed, and whenever it is replaced (once each year). This is accomplished by entering the calibration menu on the Walchem 900 main system controller. Follow the instructions. The probe must be removed for this process. Calibration is exactly like that of a standard lab pH meter. The sensor is removed by loosening the large grey plastic union using ones hands or a filter wrench (Figure 4C, Supplemental Figures 1, 4B-C). A two-point calibration is performed using both pH 7.0 and 10.0 calibration solutions (Walchem part number 51370, pH 7.00 and Walchem part number 51371, pH 10.00, Iwaki Aquatics, Holliston, MA; Supplemental Figure 4D). These calibration solutions have a limited shelf life. Be sure to rinse and dry the probe thoroughly between solutions and before reinserting it back into the sensor loop. Follow the Walchem 900 on-screen instructions. The pH probe plugs into the pH probe preamp. While the probe itself is exposed to sea water, under no circumstances can any water contact the internal preamp connections! The probe simply plugs into the upper preamp. Therefore, the pH probe must be thoroughly dried if one is replacing the pH probe element. When reinstalling the probe, turn it so that both the thin metal temperature sensor and the larger pH probe are both exposed to the cross direction of flowing water (see Supplemental Figure 4C). Retighten the PVC union to prevent leaks! Do not over-tighten this fitting. Note that unlike the conductivity sensor, the pH probe should be replaced every year. Actual system pH should be 8.3, but one may find the system readings to be off somewhat. Actual pH should be verified independently using a second device. The output pH pump set point for regulating pH level (if activated) should be adjusted accordingly to achieve the actual desired pH. Note, however, that we have not been using the pH dosing pump to regulate pH, as this was found to be unnecessary.
15.2. Calibration of the Conductivity Sensor (output to S11, Walchem #103906-10, Figure 4C, Supplemental Figure 4B, E):
The system is equipped with a Walchem contacting conductivity sensor (Figures 2, 4C, Supplemental Figure 4B, E; model number 103906-10). This sensor has a range of 0-300,000 µS, with a resolution of 10µS, but is designed specifically to monitor higher salinities (Iwaki Aquatics, Holliston, MA). The conductivity sensor must be calibrated periodically and when it is replaced. The probe must be removed for this process. Calibration is accomplished by entering the calibration menu on the main system controller. The long, thin stainless steel sensor is removed by loosening the upper-most black plastic compression nut (Figure 4C, Supplemental Figure 4E). Two adjustable wrenches are needed to ensure that the lower black plastic fitting does not come loose (Supplemental Figure 4E). To calibrate, enter the calibration menu on the main system controller. Follow the Walchem 900 on-screen instructions for calibration. A single calibration solution (Part number YSI 3167, 060907, YSI, Inc. Yellow Springs, OH) is used with a conductivity of 1000µS/cm at 25°C. These calibration solutions also have a limited shelf life. We use a shortened graduated cylinder (plastic 100ml cylinder with the top half removed) to calibrate this long sensor (Supplemental Figure 1). Be sure to rinse and dry the probe thoroughly with dH2O before and after calibration and before reinserting it back into the sensor loop. When returned back to the system, the probe is inserted all the way down into the opening. Retighten the PVC compression nut to prevent leaks! Do not over-tighten this fitting! Actual system conductivity should be around 50.6msem/cm2. tThis reading depends on the temperature (Specific gravity is equal to 1.024). The conductivity sensor should have a long lifespan of several years. Given the single point calibration, one may find the readings to be off somewhat. Actual conductivity should be verified independently using a second device. The RO pump output set point for regulating conductivity should be adjusted accordingly to achieve the actual desired level.

### 15.3. Potential Problems after Calibration!

We have found that the readings can change dramatically immediately after recalibration, even when the actual sea water parameters have not changed at all. These issues occurs for some few hours or even up to two days after calibration. Readings should eventually stabilize. However, one may need to readjust the alarm set points, as well as the set points of the appropriate control relays and monitor these over several hours or even days, using other meters to validate these readings and ensure the adjustments are correct.

**Readings made by the pH sensor can slowly drift over time, and those readings need to be carefully monitored! We have generally found these readings to get higher over time. Any adjustments need to be made accordingly! We find it best to recalibrate these probes when the readings are found to have drifted significantly. Currently, we do not rely on this sensor to make any automated system adjustments.

**The Conductivity sensor can also deliver erratic readings, and those readings need to be carefully monitored! Any adjustments need to be made accordingly! In our experience, we have found these readings to eventually stabilize after recalibration and can stay fairly constant for long periods of time. We find it best to recalibrate this probes only when the readings are found to have drifted significantly. Double check all readings using separate equipment, such as that shown in Supplemental Figure 1!

### 16. Double Checking the Sensors:

We periodically verify sensor readings using a glass thermometer, as well as handheld digital pH and conductivity meters (see List of Parts and Suppliers, as well as the tools shown in Supplemental Figure 1).

### 17. Sea Water:

The system uses Instant Ocean Reef Crystals artificial sea salt (Spectrum Brands, Inc. Blacksburg, VA, UPC code 51378 01800). This sea water is mixed using RODI to a specific gravity of 1.024 and a pH of 8.2 to 8.3 at 27°C, with the addition of Replenish (Seachem, Madison, GA), following the manufacturer’s instructions to maintain general water hardness. Note that we have found that Crepidula snails raised using the standard formulation of Instant Ocean sea salt developed shell defects (Henry et al., 2017). Instant Ocean Reef Crystals sea salt is formulated with higher concentrations of calcium and trace elements.

### 18. Bags of Crushed Coral/Shell (Figures 2, 4M):

Two nylon mesh bags (Acurel 8” x 13” Filter Lifeguard Media Bags, Acurel, Cranberry, NJ) containing a total of 15lbs of crushed coral/shell are placed to the far right side in the system sump to serve as refugia for bacteria, and as a source of calcium for added buffering and to support shell growth. There should be no need to service the crushed shell/coral, though one might inspect the mesh bags to be sure they have not split open and spilled any shell/coral debris. If any debris were to be sucked into the main pump, it would destroy the impeller. These bags can be viewed through the sump window, with the help of a flashlight (Figure 4M).

### 19. Accessing the Right Sump Compartment (Figures 2, 3A-B, Supplemental Figure 3A-C):

If it is necessary to gain access to the right sump compartment, one must remove the slotted PVC drain diverter (Figure 3A). Place the system in standby mode and let the system sit for 10 mins to allow all the water to empty back into the sump (otherwise water will drip down the back, outside of the sump once the slotted drain divertor is removed (see below). Remove the sump Origami cover (Figure 3A-B), and loosen the union joint that secures the diverter completely to remove the diverter. Remove the filter pad (It holds a lot of water, so let the pad drain on edge to allow the water to flow back into the sump, do not squeeze it dry, as you will release any trapped debris). Tilt up the entire top sump cover frame about 1-2” inches in the front, only enough to slide out the plastic, perforated filter pad plate (Supplemental Figure 3C), We have added a small plastic zip tie handle to facilitate its removal. Remember that there are several other connections to the top sump cover and one must be careful not to stress these. Reassemble all the components in the reverse order, and be careful to retighten the slotted drain diverter union to prevent any leaks.

### 20. Main Pump Inlet, (Figures 1L, 2, Supplemental Figure 2A):

Water circulation is provided by an Iwaki seal-less magnetic drive pump (MD-70RLZT) with a polypropylene centrifugal impeller (Figure 1L). Water to the pump flows through ball valve # 4 (Figure 2, Supplemental Figure 2A). This 2/7 hp pump has a rather steep pump curve with a maximum capacity of 11.4 gallons per min and a maximum head pressure of 66.6 feet. This pump can deliver a maximum system pressure of 42.7psi. The main pump inlet located within the sump should have a plastic, slotted guard to prevent large debris from blocking the opening and being sucked into the pump. This inlet guard should be swiveled to point downwards inside the sump. Inspect periodically to make sure the guard is still in place and not clogged. Note that outlet valve #4 delivers water pulled in from this opening to the main pump and should be completely open during normal operation.

The pump should never be allowed to run dry. Several safety features are built into the system to prevent this from occurring. A simple electromagnetic float valve monitors flow through a sensor loop (Figures 2, 4C). A separate flow meter also monitors flow rate through the entire system (Figures 2, 4N, Supplemental Figure 2D). If the latter sensor detects reduced flow, the pump will be turned off. Likewise, the sump has an ultrasonic water level sensor (Flowline DL10-01 Ecopod, Los Alamitos, CA; Figures 2, 4O). If the sump water level falls below a certain level, the pump will be shut off.

### 21. Pump Impeller Cavitation:

The main pump (Figures 1L, 2) is controlled by relay R1. Cavitation occurs when the main pump inlet pressure drops, and the outlet pressure rises. Under the lower inlet pressures, the inlet water can flash into steam and many bubbles will form, which then collapse violently causing shock waves that pit and erode the pump housing and impeller. This condition is very destructive. Cavitation is noted by a loud grounding noise. The sound is loud and very distinct: sounding like gravel or sand is moving through the pump. Cavitation can occur when the pump is starved of inlet water (e.g., pump inlet valve #4 is not completely open), the sump inlet cage is clogged, sump water level is too low (below the pump’s cut water level), or air has entered the inlet side from leaks in the PVC unions. Higher differential pressure on the outlet side may also cause cavitation, such as when the filters are clogged or outlet valve #1 is not completely open or there is not enough bypass water returning back to the sump via the side loop, sensor

loop or main bypass loop to help reduce outlet pressure (Figure 2, see Section 30: The Main Bypass Valve, below).

22. Drain Valve (#3) and Accessory Water Filler Tap (Valve #7) (Figures 2, 3L; Supplemental Figure 2C,E):
The rack system includes a main drain port (Valve #3), as well as a filler port (Valve #7) that can be used to remove sea water from the system, should water changes be necessary (Figures 2, 3L, Supplemental Figure 2C,E). Valve #7 and its attached blue hose (Figure 2, Supplemental Figure 2E) can be used to withdraw small or large amounts of sea water, if needed, when the system is running. Note that the water will exit with considerable pressure. This valve can also be used for partial water changes to remove water from the system (see Section 23: Automatic Mechanical Float Filler Valve). Valve #7 can also be used to drain the system to the cut level of the main pump. Likewise, drain valve #3 (Figure 3L, Supplemental Figure 2C) can be used to tap water or to empty the system, but be aware that the water will also exist with considerable pressure while the main pump is running (Not recommended!). To open this valve, one must insert the quick connector with an attached hose, and be certain to secure this hose so that it does not get loose (Figure 3L, Supplemental Figure 2J; all hoses should be secured with hose clamps!). Warning! If the main pump is running, water will leave this valve with considerable pressure. It is not recommended that valve #3 be used to drain the system while the water pump is on, as that water is under very high pressure. It is best to use the accessory filler valve (#7) for this purpose. Water can also be drained from valve #3 by gravity alone, when the pump is not running, and the system is shut off! Note that if the system is being emptied completely, any remaining water in the sump located below the opening of the main pump inlet would have to be removed from the sump by siphon or scooped/soaked up after the main pump is shut off. Do not run the main pump dry, or let the main pump suck air at any time!
23. Automatic Mechanical Float Filler Valve “FV” (for addition of sea water if the level should drop, Figure 3D):
(Currently not in use)
The sump is equipped with a simple, mechanical float valve for topping off the system, should the water level drop below a certain level (Figure 3C-D). Make sure the end of the short white tubing fitted to this valve stays elevated well above sump water level when not in use to prevent any possible leaks, as the valve opening is located at or just below the normal sump water level! Note that this valve could be used for automated or semi-manual, weekly water changes (approx. 10% per week) to reduce the levels of nitrates (see notes related to Accessory Water Filler Tap (Valve #7, Figure 2, Supplemental Figure 2E). These types of mechanical valves are somewhat unreliable, as they may stick open or closed. In addition, these float valves do not have very tight dead-bands for precise control of the water level. Therefore, we do not use this feature. Instead, we have installed an automatic top off unit that uses redundant optical sensors to detect changes in the water level and a small electromechanical pump (see below).

### 24. Float Switch (output to D3, Figures 2, 4C, Supplemental Figure 4B):

An electromechanical float switch (“ft”) senses if there is some flow in the system (Figures 2, 4C; Supplemental Figure 4B). The switch incorporates a magnetic Hall effect sensor. This component has one moving part and generally does not need any service unless it should get stuck in either the open or closed position.

25. Servicing the Paddle Wheel Flow Sensor (output to D2, Figures 2, 4N, Supplemental Figure 2D):
The system is equipped with a paddle wheel flow sensor to monitor the sea water flow rate (Figures 2, 4N). If it is necessary to remove the paddle wheel flow sensor “fm”, be sure to shut Off the system! Otherwise, this sensor will be ejected with great force! Next, drain system water as described under Section 10: Servicing the Cartridge Filters. Remove the left side grey PVC plastic sump cover (Figure 4N), angling so that any residual water will drip into the sump. Remove the stainless steel U-shaped retaining wire by pulling it to the right. This part is marked with a yellow warning tag (Figure 4N, Supplemental Figure 2D). Then pull the cylindrical sensor straight out while bracing the sensor housing with your other hand. Be careful not to jostle the PVC pipes and fittings, which are poorly supported in this area -- otherwise a leak may develop. One can rotate the sensor slightly to help ease it out. If needed, one can use a small flat blade screw driver to help pry out the sensor to get it started, but be careful not to chip/scratch the plastic. When done, reinsert the sensor and the retaining wire. Some silicone grease may be used on the sensor O-ring, if needed.

### 26. Calibration of the Echopod: Sump Water Level Sensor (output to S21, Figures 2, 4O):

An ultrasonic sensor is located in the lid of the sump to detect the sump water level (Figures 2, 4O). A long PVC tube, or “stilling well,” is attached to this sensor to keep the water level steady for more accurate readings. The water level readings can be calibrated using the main system control box, as needed, but generally no adjustments should be required once this is set up. The small exposed vent hole for the Echopod’s stilling well should be kept open. Remove any sea salts that may have dried inside this opening. The water level can also be visualized directly through the window located within the front panel of the sump (Figure 4M). Once everything has been set up, a normal operating water level line (for filtering mode) should been printed on a sticker affixed along the side of this window for quick reference. When the system’s main pump is not running, however, the sump water level may not be visible as it will rise above the top edge of this window.

### 27. Preventing Evaporation:

Seams located around the lids to the tanks and the sump, and large openings over the drainage troughs and sump, permit evaporation and salt accumulation. One should make sure that all openings are covered (Figures 1D, G-I, K; 3B; see Supplemental File 3B-D). This includes plugging the small unused holes located in the tank lids. Covers are also located on the trough drains, down spouts, the sump filter pad area (i.e., the clear plastic “Origami” cover) and above the sump heater and protein skimmer compartment. To limit evaporation from the drain troughs, we machined a set of PVC covers that contain a series of smaller holes to accept the tank drain pipes (Figure 1H-I). However, sealing the system increases system temperature, as described in Section 13: Aquarium System Temperature Regulation, above.

### 28. Sump Covers (Figures 1K, 4N):

There are two covers for openings in the top of the sump. One smaller, grey PVC plastic cover is located over the left sump compartment that houses the heater and skimmer, and was provided by Iwaki Aquatics, Inc. (Figures 1K, 4N). This cover should always remain in place and has a small slot added along the back side for the skimmer power cord. Another small hole accepts the Teflon feeding line. The right compartment that carries the coarse filter and perforated filter plate and receives the return drain water has a 1/8” thick clear polycarbonate “Origami” style cover to prevent splashing and some evaporation (Supplemental File 3D, see warnings above, regarding increasing water temperatures described in Section 13: Aquarium System Temperature Regulation). There is not a lot of room above the sump in this area and this special design was needed to fit over this opening. The Origami cover is fashioned from a single piece of 1/8 inch think polycarbonate folded on a sheet metal break (see Supplemental File 3D for diagram). In addition, a small piece of Saran wrap is first draped over the slotted PVC water diverter to cut down splashing (Supplemental Figure 3A).

### 29. Salt Creep (Figure 4G, J):

Dried sea salts will collect wherever sea water is able to escape the system (e.g., Figure 4G, J; around drains, covers, vent holes, etc.). These should periodically be removed by scraping and using a damp cloth. Significant measures have been taken here to limit the effects of water loss and salt creep (see Sections 5: Servicing Individual Tanks, 27: Preventing Evaporation, 28: Sump Covers, and 33: Automatic sea water Top-Off system).

Note also that one can lengthen the plastic tubing that supplies sea water to each tank. If the ends are located below the water surface, there will be less splashing and less salt creep will form around the lids and plugs. Keeping the tubes shorter helps with oxygenation and allows the user to more easily verify that there is water flow. The drawback to this approach is that one will not be able to easily judge how much water is flowing to the tanks, and there may be somewhat less aeration of the water.

### 30. Main Bypass Valve (V5, Figures 2, 4N-O, Supplemental Figure 2D):

The system includes a main bypass loop controlled by valve #5 (Figures 2, 4N-O; Supplemental Figure 2D). This loop/valve allows some sea water to return directly to the sump, and needs to be adjusted to prevent excessive outlet pressures and pump impeller cavitation. Outlet pressure can be monitored using the round effluent pressure gauge. Presently, during Filtering mode this pressure runs at about 10-11 PSI. During Feeding mode, it climbs to approximately 13-14 PSI. So far, we have not needed to use the bypass loop and have kept this valve #5 closed, since enough water usually returns to the sump via the tanks, side filter loop and the sensor loop. As more tanks are brought on line, there is less need to use the main bypass loop, as even greater water flow returns via the tanks, side filter loop and sensor loop. In this case, the valve can be left closed. However, if one reduces the flow to the tanks or uses a smaller number of tanks this valve would need to be opened, just enough to drop outlet pressures and to stop cavitation from occurring.

### 31. Metal Components Exposed to Sea Water (Risks of Corrosion):

Certain metal components are continuously exposed to sea water that need periodic inspection for corrosion. These include the stainless steel bolt securing the handle of the sump lid, the stainless steel outlet pressure gauge, the ferrite rotor for the automatic top off ATK pump, the stainless steel conductivity sensor, a stainless steel hose clamp securing the hose fitted to valve #7, and the stainless steel temperature probe included with the pH probe. Other parts may possibly be exposed to splashing or dripping sea water, including the stainless steel leveling feet and aluminum foot pads, the stainless steel reinforcing bands located around each fitting for the small ball valves, and the aluminum rack. Note that the titanium heater is relatively impervious to the effects of sea water.

### 32. Reverse Flow Check Valve (Figures 2, 3L; Supplemental Figure 2I):

The reverse flow check valve (“CV”) is a gravity and flow/pressure operated mechanical valve that prevents water from entering the back side of the main filter loop during the feeding mode (Figures 2, 3L; Supplemental Figure 2I). It generally should not require any service. The housing is clear plastic and one can visually inspect the valve flap to see that it opens (in filtering mode) and closes (in feeding mode) appropriately.

### 33. Automatic Sea Water Top-Off System (ATO, Figures 2, 4H-J):

This system consists of a Neptune Systems (“ATK”) Automatic Top-off Kit (ver. 2, Morgan Hill, CA) automatic top-off kit, which automatically adds artificial sea water to the sump to compensate for any drop in sea water level due to salt loss (Figures 2, 4H-J). Water spray, splashing and salt creep eventually reduce the overall volume and additional sea water must be added to raise the sump level to allow for proper operation of the protein skimmer, etc. The ATO unit consists of a microcontroller, two optical water level sensors mounted in a magnetic bracket, a small self-priming water pump (“PMUP”), plastic tubing and an anti-siphon break. The reserve sea water is stored in a 5 gallon plastic paint bucket (Figures 2, 4H-I). Two small holes are drilled into the lid to allow for passage of the two sensor wires, motor power cord and plastic water line. Freshly prepared artificial sea water is added to the bucket, but never all the way to the top (see below). Depending on the relative heights of the water in the sump vs. the external reservoir, an anti-siphon break must be installed in the tubing. The anti-siphon break must be located inside the reservoir bucket above the level of the reserve sea water! It has a small hole for the side vent that must angle downward so that ejected sea water will be directed back into the reservoir. It is normal for some sea water to be expelled from this hole during pumping. The small PMUP water pump is placed upright in the bottom of the bucket (Figure 4I). As precipitate can form in artificial sea water, a small sieve is used to protect the pump. For this purpose, we place the pump intake inside of The Republic of Tea’s “The People’s Brew Basket” (Novato, CA) nylon mesh tea strainer, which is 3” in diameter and 2-1/2” tall (Figure 4I). The 24 VDC pump has a magnetic drive impeller and was originally designed to pump RODI water. The impeller shaft has a magnetic drive impeller with an exposed ferrite rotor. These ferrite ceramic magnets have excellent corrosion resistance. We have not experienced any problems with corrosion, but it is best to periodically monitored this on a regular basis to make sure the rotor spins freely. To prevent additional pumping from occurring during a feeding cycle, which temporarily lowers the sump’s water level, the microcontroller is put on a 24 hour timer (Figure 4H), so that it only runs once each day for 30 mins (during a non-feeding, filtering cycle). For extra security, this time window is set to operate during normal working hours so that operators are more likely to be present to observe any problems that may occur with water delivery. When the unit is on a blue light will be illuminated on the microcontroller. During pumping a green light will be seen. Any problems will trigger and audible alarm and a red light will be illuminated. Whenever an alarm is sounded, the unit goes into arrest and the power must be cycled to reset the ATO.

Two optical sensors monitor water level in the sump. These are mounted in a magnetic bracket located inside the front right corner of the sump (Figures 1K, 2, 4M). The lower sensor is the main sensor and the upper sensor serves as a redundant backup, should the main sensor fail. (Due to space constraints, an additional backup in the form of a small mechanical float valve, has been removed from the bracket.) Due to the presence of the sump filter pad and sieve plate, the bracket had to be rotated 180 degrees for better clearance. This simply reverses the two optical sensor inputs that need to be plugged into the microcontroller (# 1 and #2). These two electrical plugs have been re-labeled so that they now correspond to the proper numbers on the microcontroller. The bracket for the optical sensors must be positioned at the correct height for the desired sump water level to be achieved. A strong magnet and sticky rubber pads hold the bracket in place (Figures 2, 4M). The correct water level should be located at the center of the pyramidal lens covering the main (lower-most) sensor. To get the proper adjustment, this has to be done while the system is running and during a non-feeding cycle. The course filter pad and sieve plate will need to be removed (see Section 19: Accessing the Right Sump Compartment). Once correctly positioned, the external orange magnet must not be moved. From time to time, pre-pared artificial sea water will need to be added to the 5 gallon plastic reservoir bucket. Sea water added to the system should be prepared at least a day in advance to allow the salts to dissolve and be able to adjust and stabilize the salinity. Do not mix artificial sea salts directly in the reservoir. A third optical sensor is installed in this reservoir to monitor its sea water level, and to ensure that the pump will not run dry. When low, the alarm will sound, alerting users to add more sea water. Again, if there is an alarm, the power must be interrupted to reset the system (which is normally accomplished each day by the 24 hour wall timer). This third optical sensor is held in place by a small magnet, so care is needed to make sure the position is not changed (Figure 4I). The sensor should be set approximately two inches from the bottom of the reservoir: the cut level of the small pump. There are no settings that can be adjusted on the stock ATK microcontroller; however, more complex control can be accomplished, if this unit is attached to a Neptune Systems “Apex Controller.” The plastic supply tubing from the PMUP is directed to the far right back corner of the sump (Figures 2, 4J). To allow for the passage of this tubing and the two wires for the optical sensors into the sump, a small amount has to be cut off of the very back-right corner of the removable coarse filter sieve plate. Zip ties are used to secure the tubing to the far right rear aluminum rack upright support bar (Figure 4J). Note that when combined with the Iwaki RODI pump that counters evaporation, water level can be precisely maintained to within 1-2mm inside the sump.

### 34. Feeding System (output to D5, Figure 5A):

The feeding system was constructed by Dr. Jonathan Henry, UIUC (Figure 5A-B; Supplemental Files 4-14). The feeding system consists of an Arduino Uno microcontroller (Figure 5C, Supplemental Files 4-5) that regulates the activity of a custom peristaltic pump (see below, Supplemental Files 2, 13, 14 and Figure 5B, D). The microcontroller receives several sensor inputs. These sensors determine 1) the level of food present in the food reservoir via a non-contact capacitance sensor (Figure 5E, see Supplemental File 3F-G), 2) whether food has actually been loaded into the Teflon feeding line, and 3) when food is cleared from that line to ensure accurate and complete delivery of the phytoplankton via a pulsed infrared sensor (Figure 5F, see Supplemental Files 7-12). The microcontroller also operates two 120 volt AC relays located inside a remote outlet box (Figure 5C, Supplemental Files 4-5) to 1) activate a magnetic stir plate (used to resuspend the food in the food reservoir 5 mins before feeding; Figure 5B) and 2) to activate the aquarium air-pump (used to finally purged residual food from the Teflon feeding line; Figure 5C, D). A battery backup real-time clock (RTC) reports the current time and date and lets the microcontroller know when it is time to activate and terminate the feeding cycles. Note that one may wish to reset the correct time on the RTC for any daylight savings time changes. This has to be done using a different Arduino program sketch. The timing of feeding cycles must be programmed into the Arduino microcontroller’s sketch. Note that we have currently set feeding cycles for 24 mins every 2 hours, with 2.8 ml of diluted food being delivered during each feeding (36.6ml/day, equal to equal to 2.24x10⁹ cells/ml). Since this food is pre-diluted to a strength of 75% with sterile dH2O, the actual amount of concentrated undiluted food being delivered is 2.1ml/2 hrs, or 25.2ml/day. A digital hi/low (1/0) output communicates with the Walchem 900 aquarium system controller (signal sent to solid state relay (D5) in the Walchem 900 controller) to tell the aquarium when it is time to activate a feeding cycle and redirect the filter bypass valve. Likewise, a digital hi/low (0/1) pulsed output sends a signal to the peristaltic pump to activate a pre-programmed feeding cycle. These parameters (including the number of steps (volume) and speed (steps per min) must be entered directly into the custom stepper motor controller’s memory using its joystick interface (see Supplemental Files 13-14). Once set, these pumping programs are non-volatile and are stored permanently in memory, to be recalled in the event of a power failure. Thus, there is no need to adjust the feeding system if the power should cycle.

The feeding system microcontroller has an illuminated push button power switch (Figure 5C). When the system is on and in a non-feeding (filtering) cycle this light will be green. When the system is on and in a feeding cycle (non-filtering) the light will turn blue. If a fault is detected and an alarm is triggered, the light will be red.

The feeding system’s Arduino Uno also has an attached ethernet shield, which can be connected to a computer network. Text messages and/or emails will be sent to predefined users: whenever, 1) the food becomes too low in the food reservoir, 2) when no food is loaded into the Teflon feeding line, and 3) if the food is not completely cleared from the Teflon feeding line.

Please note that the alarm indicator light A3 for feeding cycles on the Walchem 900 controller (actually an indicator of the position of the bypass valve) is only activated when the bypass loop valve is actually in the bypass (feeding) position. This differs from the regular vs. feeding mode indication provided on-line through the V-touch server portal, which depends on the state currently being sent by the feeding controller (to D5). Unless someone has gone into the Walchem controller to change these states, they should be the same. Note that if the power were to be interrupted during a feeding cycle, the system would revert back to a non-feeding (filtering) mode, until the next feeding cycle is triggered.

For the peristaltic pump, we purchased a small pump head and stepper motor and developed our own custom stepper motor microcontroller circuit and program (See Supplemental Files 2, and 13-14). The pump head accepts a short length of 4mm OD x 2mm ID silicone tubing, which is connected to barbed Luer lock hose adapters, a single Luer lock Y connector and a one-way check valve (Qosina, Cole-Parmer, Vernon Hills, IL). Together, these create a pump to withdraw food from a reservoir and dispense this to the aquarium system (Figure 5B-D, and Supplemental File 2). The food is ultimately passed to the aquarium system through 1/8” Teflon tubing. A special flangeless compression fitting is used to attach the 1/8” Teflon tubing to this valve system (HPLC waste line adapter, HPLC-LL-1/8-KIT; CPLabSafety, San Francisco, CA; Figure 5D). This tubing is directed to the left sump compartment through a hole drilled in the top of the small removable PVC sump cover located directly above the aquarium system main water pump intake (Figures 2, 4N). Note that the silicone tubing and other parts (Figure 5D) will need to be sanitized and/or replaced periodically. Any problems in the delivery of the food will be detected by the IR food line sensor (Supplemental Files 9-12) and users will be alerted to the problem via email and text messages, and they should correct the issue as soon as possible. Such problems typically involve only one or both of the feeding valves. For cleaning, parts of the feeding system including the silicone tubing, Luer lock connections, supply tube and Teflon feeding line should be removed, rinsed several times with sterile dH2O and finally cleaned with 2-3 rinsed of 70% ethanol. After cleaning, the parts should be dried and reassembled. Parts should be checked to make sure they are tight. These inexpensive parts should be replaced every 6-12 months or sooner, as needed. At the same time, the food reservoir should be cleaned, autoclaved and refilled with fresh food.

We dilute the food to a 75% concentration with sterile dH2O. It is important to prime the feeding pump to make sure the food is flowing properly. In any case, users will be alerted when there are problems with food delivery via an email or text message.

Formerly, we tried using a syringe pump to deliver the food, but this required a more elaborate arrangement of parts and was prone to problems involving air bubbles. The use of the peristaltic pump has proven to be very reliable and precise in terms of the volume of food that is delivered. Furthermore, this setup is less costly. One note of caution, however, as the silicone tubing wears out the volume delivered may change. Peristaltic pumps that use stepper motors are ideal as they produce high torque with precise degrees of rotation. The same input from the main feeding controller is used to trigger a preset number of steps (at the preset speed (rpms)) to deliver the correct, pre-calibrated volume of food. The volume of food will depend on the diameter of the silicone tubing used in the peristaltic pump. Therefore, one will have to calibrate the volume and number of steps needed to deliver the desired amount of food. The stepper motor has 200 steps per revolution and is rated for no more than 60RPM. We generally set the speed to 50RPM.

### 35. General Leaks:

Water leaks may form at any time. It may be prudent to place the system in standby mode to inspect and repair these leaks. If these leaks occur at various PVC fittings or unions they need to be inspected and tightened. Look for any cracks, and use the appropriate tools to service these parts (see Supplemental Figure 1). Generally, these are to be hand-tightened, but a little coaxing with a wrench may be required. Silicone rubber kitchen jar pads are useful for getting a slip-proof grip for loosening or hand-tightening these parts. Alternatively, one can use the Channel Lock oil filter/PVC wrench (Channellock, Inc., Meadville, PA) to tighten or loosen these fittings. Excessive force should be avoided, so as not to damage the plumbing. Over-tightening these parts may cause them to crack or seize.

### 36. Dripping Valves:

Occasionally, a ball valve may drip when it is supposed to be shut off, or a valve may not provide sufficient flow, and these valves may need to be tightened or cleaned. To service the larger ball valves with red handles, one must use an adjustable wrench and a special ½” valve seal carrier key, TSK 1-005, to tighten the valve seat (Supplemental Figure 1). This is done by loosening the union and accessing the seat through the main valve opening where it can be tightened using the key (follow the manufacturer’s instructions). For the smaller ball valves that serve each tank (with the blue handles), no adjustments can be made. One would simply have to replace those valves. This requires that one loosen the entire valve manifold at its union so you can rotate the manifold downward, which will then allow the valve to be unscrewed and replaced. Teflon tape is used to help seal these small valve threads.
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

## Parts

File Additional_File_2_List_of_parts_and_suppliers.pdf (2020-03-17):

List of Parts and Suppliers for Components used in the Aquatic Rack System: (Henry Lab, UIUC)

Additional File 2

Jonathan Q. Henry, Maryna P. Lesoway, Kimberly J. Perry

Department of Cell & Developmental Biology University of Illinois
601 South Goodwin Ave.
Urbana, IL 61801

Ver. March 16, 2020

Figure notations (Figures 1-5) refer to those included in Henry et al. (2020), and additional figures (Figures S1-S4 are supplemental figures included with Additional File 1, SOP). Other file references include correspondingly numbered Additional Files that also accompany Henry et al., (2020), which are all available at https://github.com/HenryLabUIUC/Automated-Aquatic-System.

Feeding system peristaltic food pump, and associated parts (to deliver the food), Figure 4A-D:

1 x 120 Can beverage cooler (mini-refrigerator), stainless steel with glass door (model no. DBC120BLS, Danby Products, Inc., Guelph, Ontario, Canada). Figure 5A.
Used to maintain the food and feeding pump equipment at 4°C. Note that a 1”-3/8” dia. hole has to be drilled through the back side wall, just to the left side above the compressor compartment to permit access for various power cords, the airline and control cables. This hole can be drilled straight down (in a direction towards the floor), using a hole saw, starting from the inside, through the plastic liner, insulation and finally the sheet metal. Exposed sharp sheet metal edges must be covered with grommets to prevent cutting of the cords and any shock hazard. Once the cables are routed, the hole should be packed with foam insulation. An additional 1/8” dia. hole has to be drilled though the left or right side of the cabinet (plastic liner, insulation and sheet metal) to allow passage of the Teflon food line. WARNING! The location of this small hole is critical, so as not to puncture the cooling and heat exchange coils. On this particular model it is safe to drill this tiny hole either on the left or right side (3-1/4” down from the top surface of the outer cabinet and 5-1/4” back from the front surface of the outer cabinet (not including the door)).

1 x Peristaltic pump with stepper motor (Peristaltic pump with 42 stepper motor dosing tubing hose pump small flow 0-160ml/min (with 42 motor), INZOK, https://www.amazon.com/Peristaltic-Stepper-Dosing-Tubing-0-160ML/dp/B07PYR2P7K?th=1) see Figure 5D.

Used as a precise means of delivering the food. Pumping speed (steps per min. and volume (i.e., number of steps) are entered directly into the peristaltic pump controller. Note that even though the motor is listed as a “42 stepper motor,” it is supplied as a 1.8 degrees per step or 200 steps per revolution stepper motor, which is ideal and permits fine volume control.

Silicone tubing (4mm OD x 2mm ID, or similar). Various sources. (e.g., part no. EW-96201-33, Ultra Platinum Silicone tubing, 5/64 ID x 9/64 OD, 25 feet part no. EW-96201-33, Cole Parmer, Vernon Hills, IL).
One piece is supplied with the peristaltic pump, but replacement tubing will be required. High quality tubing lasts for a very long time, but eventually it will become stretched and its elasticity will change as it wears out. This can lead to gradual changes in the volume that is being delivered. Six inches of tubing is used for the pump. See note about tubing connections, below.

1 x Luer lock Y connector with spin lock (part no. 90190, Qosina, Ronkonkoma, NY).
Used to assemble the food pump and to inject air into the feeding line. This part has two female Luer lock fill ports and a single male Luer lock connector with a spin lock.

1 x HPLC waste line adapter (part no. HPLC-LL-1/8-KIT; CPLabSafety, San Francisco, CA). Used as part of the food pump to connect the Teflon feeding line to very end of the Y connector.

PTFE, Teflon tubing (feeding line; 6-8 feet long, as needed) 1/16” ID, 1/8” OD. (part no. 53XL53, Grainger Industrial Supply, Alsip, IL)
Used as part of the food pump to deliver food to the sump compartment. Length should be kept to a minimum.

2 x 1/8” Barbed to male Luer lock connectors. (part no. 11525, Qosina, Ronkonkoma, NY) Used to attach the silicone tubing to the Luer lock Y connector and the airline tubing to the Luer lock one-way check valve, listed below. Note that a fine wire may be used to prevent the silicone tubing from slipping off the barbed connector by twisting this tightly around the tubing just below the flared, barbed end of the connector (like a fine twist tie). Do not over-tighten this wire, as it could cut through the silicone tubing.

1 x 1/8” Barbed to female Luer lock connector. (part no. 11524, Qosina, Ronkonkoma, NY) Used to attach the silicone tubing to the reservoir tubing. Note that a fine wire may be used to prevent the silicone tubing from slipping off the barbed connector by twisting this tightly around the tubing just below the flared, barbed end of the connector (like a fine twist tie). Do not over-tighten this wire, as it could cut through the silicone tubing.

1 x Luer lock tubing (900 SPI 3/16 OD x 48” long, part no. 30526-28 Cole Parmer, Vernon Hills, IL).
Used to draw food from the reservoir. Has both male and female ends. Cut off the female end, and use only the remaining tubing with the male end. Trim this tubing as short as possible so that the cut end just reaches the bottom of the reservoir.

1 x Small aluminum box (BUD Industries, Inc., part number CU-234)

Used to mount the peristaltic pump. A square opening must be machined in the lid of the box with screw holes for mounting the peristaltic pump. Another hole must be drilled to accommodate the cable gland.

1 x Water proof cable gland for cable, PG7 size. Various suppliers, (https://www.amazon.com/Connectors-Plastic-Protectors-Waterproof-Adjustable/dp/B07RHJM435/ref=sr_1_9?keywords=cable+glands&qid=1572968857&sr=8-9) Used to secure the cable and prevent water incursion into the aluminum project box.

1 x 1000 ml screw top Pyrex bottle (part no. 1395, Corning, Germany). Figure 5E.
Used as the food reservoir. A hole can be drilled in the screw cap to accept the trimmed Luer lock tubing.

1 x Teflon stir bar. 1” long. (part no. 1451351, Thermo Fisher Scientific, )
Used to resuspend the food.

1 x small 5” x 7” magnetic stir plate (part no. CLS6795410D. Corning, Tewksbury, MA). Figure 5B.
Used to resuspend the food.

1 x Machined ½” diameter, by 9 inches long aluminum rod and adjustable bracket. Bar has threaded end (1/4” – 20). Used to hold the capacitive sensor that detects the presence of food in the food reservoir. Adjustable bracket has a clamping screw to secure its position (height) on the bar. (These parts mount directly onto the stir plate, which has a threaded hole on the back. (See Additional File 3F-H, Figure 5E).

Feeding system air injection parts (to purge the feeding line), Figure 5C,D:

1 x Air Pump (Uniclife part no. UL40, 4.0 watts, 4.0 L/min, 0.016 MPa pressure, dual twin outlet air pump, or equivalent, Uniclife, https://www.amazon.com/Uniclife-Aquarium-Outlets-Accessories-Adjustable/dp/B01EBXI7PG/ref=zg_bs_2975471011_2?_encoding=UTF8&psc=1&refRID=HH XH8MKDCFSMQQ7KKVQ7). Figure 5C.
Used to purge the feeding line of residual food. (Use both pump channels joined with a barbed Y connector for maximum air pressure needed to purge the Teflon feeding line).

1 x Clear aquarium airline tubing (approx., 3/16” OD x 6 feet long).
Used to supply air from the air pump to purge the feeding line. It is attached to a barbed Luer lock connector (see above). (This tubing is supplied as two pieces with the Uniclife air pump)

1 x Barbed dual-ended straight connector.
Used to connect the two airline tubing pieces together (supplied with the Uniclife air pump)

1 x Barbed Y connector.

Used to connect both air pump, air channels together to increase air pressure (supplied with the Uniclife air pump. Cut two short 2 inch long pieces off of the clear airline tubing to connect this Y connector to the pump outlets)

1 x Luer lock one-way check valve, female to male (SAN plastic with silicone diaphragm, pack of 10, part no. UX-30505-92, Cole-Parmer, Vernon Hills, IL). Cracking pressure = 0.174psi (part no. 11582, Qosina, Ronkonkoma, NY). Cracking pressure = 0.217psi. Used as a key part of the food pump: As an alternative, a duckbill check valve can be used (part no. 80065, Qosina, Ronkonkoma, NY). Cracking pressure = 0.433 psi. These provide a good seal to prevent backflow.
Used as part of the food pump to prevent liquid food from entering the purge airline. This part is connected to the Y connector (one can use two of these check valves in series, if desired, for extra security, though this does not appear to be necessary).

Feeding System Micro-controller: (to regulate automated feeding), Figure 5C:

To build this microcontroller unit please see instructions, fritzing diagram (“Feeding controller2.fzz”) and Arduino program sketch (“aquarium_feeding_controller9IRFinal copyl.int” program file). See Additional Files 4-5 and Figure 4C.

3 Wire Capacitive Proximity Sensor Switch (4cm dia.; part no. 1 x Ljc30a3-h-z/bx Dc, Uxcell, https://www.amazon.com/dp/B0147XIWE6
This part has its own three conductor cable. Used to detect food in the reservoir. This part is held in position using the bracket described in Additional File 3F-H.

1 x USB + Serial Backpack Kit with 16x2 RGB backlight positive LCD - Black on RGB (Adafruit product no: 782. https://www.adafruit.com/product/782)
Used to display the time, date and status of the feeding cycles.

1 x Plastic bezel for LCD display (3D printed decorative plate to cover exposed edges of the LCD display and opening on the microcontroller housing. See “LCD_Bezel_98.stl” see Additional File 6).

1 x 9 VDC 1000mA switching power supply. This wall transformer has a 2.1mm dia. center positive male power plug. (Adafruit product no. 63, https://www.adafruit.com/product/63). Used to provide power to the microcontroller unit.

1 x 19mm dia. RGB LED illuminated On-Off push button switch. (Adafruit product no. 3426, Adafruit. https://www.adafruit.com/product/3426).
Used to control power to the microcontroller unit and to display feeding system status via the built in LEDs.

1 x Arduino Uno microcontroller (SMD version, https://www.amazon.com/dp/B007R9TUJE/). Used to regulate the feeding cycles and communicate with the Walchem 900 controller.

1 x Arduino Ethernet Shield (SunFounder Ethernet Shield W5100 for Arduino UNO R3 Mega product no. 2560 1280 A057, https://www.amazon.com/dp/B00HG82V1A). Used for an internet connection to relay various faults to the users. Note that there are different versions of the Wiznet ethernet chip. The Arduino program is designed to work with the W5100 chip, which is a slightly older chip. Some other chips are not compatible with the libraries used for compiling the Arduino program, and would require a slightly different script

1 x PCF8523 Real Time Clock (Adafruit product no. 3295, https://www.adafruit.com/product/3295).
Used as an internal clock to time the feeding cycles.

1 x 3 volt CR1220 Battery for Real Time Clock (RTC). (Adafruit product no. 380, https://www.adafruit.com/product/380)
Used to provide power to the real time clock. This should last for 4-5 years.

1 x small solderable copper plated perf board 1-7/8” x 2’1/4’ (Circuit Specialists, Tempe, AZ, part no. 64-8932).
Used to mount various electronic components, the optocouplers and terminal blocks)

2x 10K resistors, ¼ watt, various suppliers.

1 x 2.2K resistor, ¼ watt, various suppliers.

5x 1K resistors, ¼ watt, various suppliers.

2 x MCT2E optocouplers (part no. MCT2E-ND, Digikey, https://www.digikey.com/products/en?keywords=MCT2E-ND). Used for switching and electrical isolation of various parts.

2 x 6 pin DIP socket (part no. 571-1-2199298-1, Mouser Electronics, https://www.mouser.com/ProductDetail/TE-Connectivity/1-2199298-1?qs=fK8dlpkaUMsQ%252BTzExsKLsw%3D%3D)
Used for mounting the optocouplers.

4 x 2-pin terminal blocks (Adafruit product no. ID 724, https://www.adafruit.com/product/724). Used for ease in wiring internal connections to the various data cables.

6 x nuts and machine screws of 4-40 size, 1/2” long, various suppliers.
Used for mounting the Arduino Uno and perf board.

4 x 2-56 machine screws, 1/4” long, various suppliers.
Used to secure the LCD.

6 Plastic standoffs, for 4-40 machine screws, 3-4mm long, various suppliers. Used to mount the Arduino Uno and perf board.

2 small plastic standoffs for use with the 2-56 machine screws, 2mm long, various suppliers. Used to mount the LCD.

24 gage insulated hook up wire, various suppliers.
Used for various electrical connections.

1 x Project box, 5.3” x 3” x 1.9” (part no. MB-113, All Electronics, Van Nuys, CA, https://www.allelectronics.com/item/mb-113/abs-project-box-5.3-x-3-x-1.9/1.html).
Used to house the relay module and outlets. Note that various openings will need to be machined to permit mounting of various components.

Used to house parts for the microcontroller. Note that various openings will need to be machined to permit mounting of various components.

5 x Water proof cable glands for cables, PG7 size. Various suppliers, (https://www.amazon.com/Connectors-Plastic-Protectors-Waterproof-Adjustable/dp/B07RHJM435/ref=sr_1_9?keywords=cable+glands&qid=1572968857&sr=8-9) Used to secure the cables and prevent water incursion into the microcontroller project box.

4 conductor cable (18 feet), various suppliers
Used to connect the microcontroller to the stepper motor controller and Walchem 900 controller.

DB9 connector (9 pin male), various suppliers
Used to connect the microcontroller to the stepper motor controller.

Heat shrink tubing, various suppliers
Used to insulate various connections.

Remote relay outlet box to control power for the air pump and the stir plate, (Figure 5C):

4 conductor cable (6 feet), various suppliers
Used to connect the relay box to the microcontroller.

1 x Three prong grounded 120 volt dual power outlet, 8 feet long, various suppliers
Used to provide 120VAC power to the switched outlets for the air pump and stir plate. Note that the common hot wire connection between the two outlets has to be cut, as they are separately controlled by the relay module.

1 x Relay module (part no. MCIGICM 2 Channel DC 5V Relay Module for Arduino UNO R3 DSP ARM PIC AVR STM32 Raspberry Pi with Optocoupler Low Level Trigger Expansion Board, https://www.amazon.com/dp/B072BY3KJF).
Used to regulate power to the two outlets.

2 x Waterproof cable glands for cables to prevent water incursion. Need 1 x PG7 and 1 x PG9 sizes, various suppliers (see above).
Used to secure the cables and prevent water incursion into the outlet box.

1 x Project box, 5.3” x 3” x 1.9” (part no. MB-113, All Electronics, Van Nuys, CA, https://www.allelectronics.com/item/mb-113/abs-project-box-5.3-x-3-x-1.9/1.html).
Used to house the relay module and outlets. Note that various openings will need to be machined to permit mounting of various components.

1/2" self-adhesive Kwik Klips, adjustable cable clips (Used for managing electrical cords on the feeding and aquarium systems. (GKK0-1550 Kwik Klips, https://www.amazon.com/dp/B00002NAOE).
Used for external cable management around the system.

Mounting bracket for feeding system microcontroller unit, includes two 3D printed parts: (see Articulated arm base plate .stl files included in, Additional Files 7-8, and available on Henry Lab web site, www.life.illinois.edu/henry). Note that other arrangements can also be made for mounting the microcontroller. Figure 5C:

1 x Articulated Arm, all metal construction, Camvate 7” (147mm) articulated arm V1 black and red, with ¼-20 threads. (Camvate, https://www.amazon.com/dp/B017OTDZTM). Figure 5C. Used with the two 3D printed parts, detailed below, to position the microcontroller, see Additional Files 7-8.

1 x Plastic circular, beveled plate (has center tapped with ¼-20 hole for articulated arm) to be affixed to the control box by heavy duty double stick foam tape. (see “Articulated arm base plate v10.stl” file provided).

1 x Semi-circular mounting plate (has center taped ¼-20 hole for articulated arm). Two counterbored holes accept 10-32 cap screws for mounting this plate on the top of the beverage cooler using the unused door hinge threaded holes on the top of the mini refrigerator. Door is reversible so either left or right side can be used, but be aware of the arrangement of cables to best mount the arm. (See “Articulated arm base plate v10.stl” file provided).

External feed line sensor (Monitors food delivery, see documents provided in a separate file), Figure 5F:

1x Teflon feeding line clamp consisting of two parts, base and top (See “tubing holder v2.stl” files provided). See Additional Files 9-10.
Used to mount the IR LED and sensor.

1 x 5mm IR LED (Adafruit product ID 387, https://www.adafruit.com/product/387).
Used as a pulsed source of IR light.
This part is mounted (glued into) to the base of the food line clamp.

IR 38Mhz detector, TSOP4838 (Jameco part no. 2229351 (or TSOP1839), Jameco Electronics. Belmont, CA https://www.jameco.com/shop/ProductDisplay?catalogId=10001&langId=-1&storeId=10001&productId=2229351)

This part is mounted (glued into and secured with a screw-on retaining strap) to the base of the food line clamp.

Retaining straps (See “retaining strap v3.stl” file provided) See Additional Files 11-12.

2 x Water proof cable glands for cables to prevent water incursion. PG7 size, various suppliers. See above.
Used to secure the cables and prevent water incursion into the box.

4 conductor cable (6 feet), various suppliers
Used to connect the remote sensor to the microcontroller.

1 x Small water-proof box (BUD Industries, Inc., part number PN-1320)
Used to protect the components of the IR sensor.

Peristaltic Food Pump Stepper Motor Controller: (used to regulate food delivery), Figure 5C:

To build this microcontroller unit please see instructions, fritzing diagram (“peristaltic_pump_controller.fzz”) and Arduino program sketch (“stepper_motor_controller.int” program file). See Additional Files 13-14 and Figure 5C.

1 x Arduino Uno microcontroller (SMD version, https://www.amazon.com/dp/B007R9TUJE/). Used to regulate food delivery and communicate with the Walchem 900 controller.

1 x USB + Serial Backpack Kit with 16x2 RGB backlight positive LCD - Black on RGB (Adafruit product no: 782. https://www.adafruit.com/product/782)
Used to display the settings (i.e., speed, and number of steps) for the stepper motor.

1 x Project box, 5.3” x 3” x 1.9” (part no. MB-113, All Electronics, Van Nuys, CA, https://www.allelectronics.com/item/mb-113/abs-project-box-5.3-x-3-x-1.9/1.html).
Used to house the relay module and outlets. Note that various openings will need to be machined to permit mounting of various components.

1x 10K resistor, ¼ watt, various suppliers.

1 x Analog 2-axis joystick with select button and breakout board. (Adafruit product no. 512, https://www.adafruit.com/product/512).
Used to input settings for speed and number of steps.

1 x small solderable copper plated perf board 1-7/8” x 2’1/4’ (Circuit Specialists, Tempe, AZ, part no. 64-8932).
Used to mount electronic components, and to make various wire connections.

1 x Plastic bezel for LCD display (3D printed decorative plate to cover exposed edges of the LCD display and opening on the microcontroller housing. See “LCD_Bezel_98.stl” see Additional File 6).

4 conductor cable (8 feet), various suppliers
Used to connect the stepper motor controller’s microcontroller to the Feeding system’s microcontroller and to the stepper motor in the peristaltic food pump, which is located inside the mini-refrigerator.

1 x DB9 connector (9 pin female), various suppliers
Used to connect the microcontroller to the feeding controller.

1 x 9 VDC 1000mA switching power supply. This wall transformer has a 2.1mm dia. center positive male power plug. (Adafruit product no. 63, https://www.adafruit.com/product/63). Used to provide power to the microcontroller unit.

2 x Waterproof cable glands for cables to prevent water incursion. Need 2 x PG7 size, various suppliers (see above).
Used to secure the cables and prevent water incursion into the project box.

6 x nuts and machine screws of 4-40 size, 1/2” long, various suppliers.
Used for mounting the Arduino Uno and perf board.

4 x 2-56 machine screws, 1/4” long, various suppliers.
Used to secure the LCD.

6 x Plastic standoffs, for 4-40 machine screws, 3-4mm long, various suppliers.
Used to mount the Arduino Uno and perf board.

2 x small plastic standoffs for use with the 2-56 machine screws, 2mm long, various suppliers. Used to mount the LCD.

24 gage insulated hook up wire, various suppliers.
Used for various electrical connections.

1 x 16mm dia. Green LED illuminated On-Off push button switch. (Adafruit product no. 482, Adafruit. https://www.adafruit.com/product/482).
Used to control power to the microcontroller unit.

Protein Skimmer (Used to remove uneaten food and dissolved organic material), Figure 3C-F:

1 x Tunze Comline 9004 DC DOC skimmer (DC motor version with DC motor controller) (Tunze, Penzberg, Germany). Figure 3C.

1 x Plastic bulkhead connector single port, for 3/8” OD silicon tubing, with NPT threaded connector (5694T161, McMaster Carr, Elmhurst, IL) and ½” ID 3.32 O-ring and Teflon tape. Corresponding ¼” NPT threaded nut and ½” ID 3.32 O-ring and Teflon tape to seal connection. Hole for this fitting is drilled into side of Tunze collecting cup towards the bottom. Inner shoulder located in the central passage way of this of fitting is drilled out to allow for complete thru passage of the silicone tubing.
Used as a continuous drain connection for the collecting cup silicone tubing.

1 x Plastic bulkhead connector dual ports, for 3/8” OD silicon tubing (To be installed in the side wall of the sump (Figure 3F). 5694T17, McMaster Carr, Elmhurst, IL). Inner shoulder located in the central passage way of this fitting is drilled out to allow for complete through passage of the silicone tubing.
Used to allow for passage of the silicone skimmer drain line through the wall of the sump.

Silicone tubing, Silastic Laboratory Tubing, Four feet long, 0.188” ID x 0.375” OD. (part no. 515-014, Dow Corning, Midland, MI).
Used as a drain tube for the collecting cup.

Custom motor control interface (regulates power to the protein skimmer via the Walchem 900 controller), Figure 5G:
Fritzing diagram (“DC motor controller interface2.fzz”) for assembling the circuit, and program for the ATtiny85 chip (“ATtiny_motor_controller copy.ino”). See files provided in Additional Files 15-16.
Used to automatically turn off protein skimmer during feeding.

Fine insulated wire, size 30, solid strand, any 30 gauge wire wrapping wire should work (https://www.amazon.com/dp/B07WRTWWZW)

1x ATtiny85 operating at 1MHz (Sparkfun, COM-09378, https://www.sparkfun.com/products/9378). Note this is programmed using Arduino IDE and SparkFun Tiny AVR Programmer (see below).

Tiny AVR Programmer (part no. PGM-11801, https://www.sparkfun.com/products/11801). Required to program the ATtiny85, above.

3x 10K resistors, ¼ watt, various suppliers

3x 1K resistors, ¼ watt, various suppliers

1 x Zener diode *removed from DC motor control board (see Figure 5H, details published in Henry et al., 2019).

1 x MCT2E optocouplers (part no. MCT2E-ND, Digikey, part no. MCT2E-ND, Digikey, https://www.digikey.com/products/en?keywords=MCT2E-ND).
Used for switching and electrical isolation of various parts.

1 x 6 pin DIP socket (part no. 571-1-2199298-1, Mouser Electronics, https://www.mouser.com/ProductDetail/TE-Connectivity/1-2199298-1?qs=fK8dlpkaUMsQ%252BTzExsKLsw%3D%3D)
Used for mounting the optocoupler.

1 x 8 pin DIP socket.
Used for mounting the ATtiny85 chip.

1 x 10µf capacitor.

1 x small solderable copper plated perf board 1-7/8” x 2’1/4’ (Circuit Specialists, Tempe, AZ, part no. 64-8932). Trim to fit inside housing.
Used to mount various electronic components, the optocouplers and terminal blocks..

1x custom cut insulating thin plastic sheet (same size as perf board)
Used as insulation.

4 conductor cable (8 feet), various suppliers
Used for connecting the interface to the Walchem 900 controller.

24 gauge insulated hook up wire

2 x Rubber grommets (5/16” OD)
Used to secure the cable, provide strain relief and prevent water incursion into the housing.

2 x small zip ties, various suppliers
Used to secure the cables.

3D printed housing and cover plate to enclose the circuit (See 3D printer stl file: “control box v7.stl” provided). See Additional Files 17-18.
Note that once installed the lid can be secured using a small amount of silicone cement.

Additional components needed for the rack system (e.g., sea salts, media for the various filters, and components needed to culture small animals, and to reduce splashing, evaporation and to regulate sea water level): Note, most of the standard components that make up the rack system provided by Iwaki Aquatics, are not listed here.

Instant Ocean Reef Crystals artificial sea salt (Spectrum Brands, Inc. Blacksburg, VA, UPC code 51378 01800).
Used as the artificial sea salts to prepare the sea water, following the manufacturer’s instructions. Seed Bacteria (Aquavitro, Seachem, Madison, GA) or Dr. Tim’s One and Only Live Nitrifying Bacteria (Dr .Tim’s Aquatics, LTD, Moorpark, CA).
Used initially to seed the biofilter.

“Marine Buffer” (Seachem, Madison, GA).
Used to raise the pH of the sea water, as needed.

Filters and filter media

Two Acurel Filter lifeguard media bags, 9” x 13” (prod. ID 42982 08033, Acurel, Cranbury, NJ). Placed inside the right-hand sump compartment and used to contain the crushed shell and coral, so that these course debris cannot escape and enter the water pump and filters. These bags should be securely tied shut once filled.

Crushed coral (Geo-Marine Argonite formula 15lb bag. Product ID 0847900120, CaribSea, White City, FL).
Used as a source of calcium and as a buffer for the sea water. The substrate is placed inside two fine mesh bags, above, which go into the right sump compartment, so that the coarse debris cannot enter the water pump and filters.

Biological filter media consisting of a mix of 800 gm of Matrix (Seachem, Madison, GA) and 100 gm of de*Nitrate (Seachem, Madison, GA).
Used as a substrate to support aerobic, anaerobic and facultative bacteria growth.

1-2 lbs of activated carbon pellets (Kent Reef Carbon Pellets, Kent Marine, Franklin, WI). Used to remove dissolved organic compounds from the sea water.

Polyhydroxyalkanoate (PHA) polymer pellets (Vertex Aquaristik Pro-Bio Pellets, Huntington Beach, CA).
Used to support nitrifying bacteria, should be replenished, as needed.

Replenish, (Seachem, Madison, GA).
Used to restore general hardness to RODI.

Automatic top off unit to add sea water, Figure 4H-I:

System automatic top off unit (ATK unit, Neptune Systems, Morgan Hill, CA). Used to automatically add sea water. Figure 4H.

Optical sensor with magnetic mount (OS-1-M, Neptune Systems, Morgan Hill, CA). Used to monitor the level of sea water inside the reservoir. Figure 4I.

Small nylon basket (“The People’s Brew Basket”, The Republic of Tea, Novato, CA). Used as a filter to prevent debris and ppt from entering the small ATK PMUP water pump. Figure 4I.

Clean 5 gallon plastic paint bucket with lid, various suppliers.
Used as the reservoir for the sea water. Note that small holes need to be drilled through the lid to allow for the passage of the power cord, optical sensor cable and plastic tubing. Figure 4H.

Parts to help limit evaporation and water loss:

1/2” Off-white plastic snap in plugs for panels with tapered prongs (need 200) off-white color. Used to cover the 1/2" holes in tank lids. (Part no. 9688K251; 100 pcs each, 9688K25162PP050BG14, McMaster Carr, Elmhurst, IL.). Figure 1G.

Custom machined 1/4” thick PVC covers for the drain troughs (See Additional File 3B-C). Figure 1H-I.

Polycarbonate “Origami” cover for the large sump drain opening (See Additional File 3D, Figure 3B.

Culture tubes for animals:

Ultra-stiff mesh plastic canvas (for needle point). (#7 mesh = openings per inch). Used to create a curved barrier to keep culture tubes submerged inside the small tanks. Darice Canvas 3pc. Designer Ultra stiff Canvas 12”x18” (product ID 826709455). Darice, Inc. Strongsville, OH. Each piece can be cut with scissors to make two barriers (20cm x 22.5cm). Figure 1D, J.

Screened culture tubes (See Henry et al., 2017). Small culture chambers to contain animals are constructed from either 50ml or 15ml screw top polypropylene tubes (Corning # 430897 (50ml) and Nunc # 339651 (15ml) Corning Inc., Corning, NY; and Nalgene Nunc, Rochester, NY, respectively), with open ends covered by fiberglass screens (see Henry et al., 2017). Figure 1D.

External Chiller, Figure 4K:

1 x Artica Titanium Chiller, part no. DBA-075 (JBJ Aquarium, Inglewood, CA). Used to lower sea water temperature. Figure 4K.

2 x Custom machined PVC adapters for the water chiller (See documents provided in a separate file). (See Additional File 3E).
Used to adapt chiller water connections to 3/8” plastic tubing. Figure 4L.

3/8” OD tubing by ¼ NPT male threaded right angle polypropylene compression fittings (part no. 9087K23, McMaster Carr, Elmhurst, IL). Needed to hook up the plastic tubing. Figure 4L.

2 x Sets of clamps/bolts/cables to secure the rack.
Used to secure the top of the rack and prevent it from tipping over. Exact parts depend on where the rack is located and what supports are available to attach these parts. Figure 1B.

4 x Custom machined ½ inch thick, 4” x 4” square aluminum foot pads. Each has a central 1/8” deep by 1’ -3/8” dia. recess for the leveling feet.
Used to distribute the weight of the rack system. Figure 1C.

Useful/Essential tools (needed to service the system): Additional File 1: Figure S1.
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

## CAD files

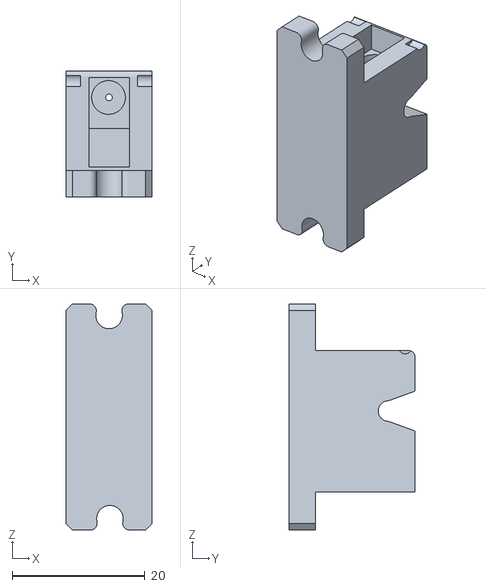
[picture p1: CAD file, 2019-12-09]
Additional_File_9_Tubing_holder_base.stl
13.0 x 19.0 x 34.0

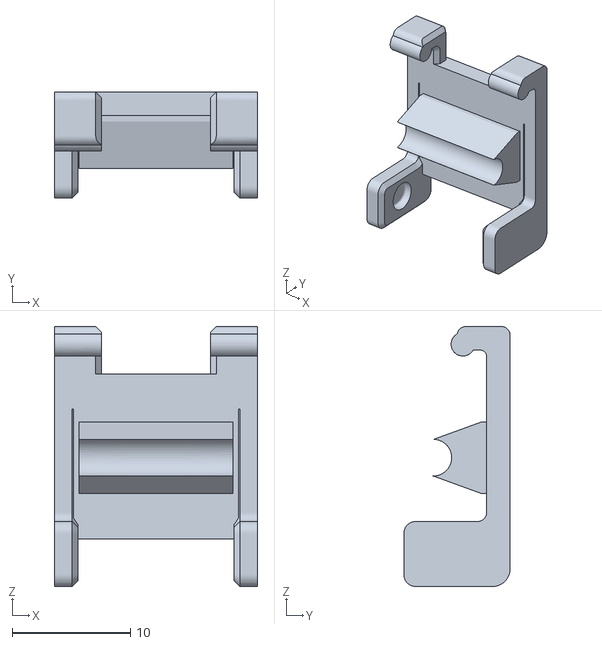
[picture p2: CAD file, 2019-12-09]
Additional_File_10_Tubing_holder_top.stl
17.2 x 9.00 x 22.0

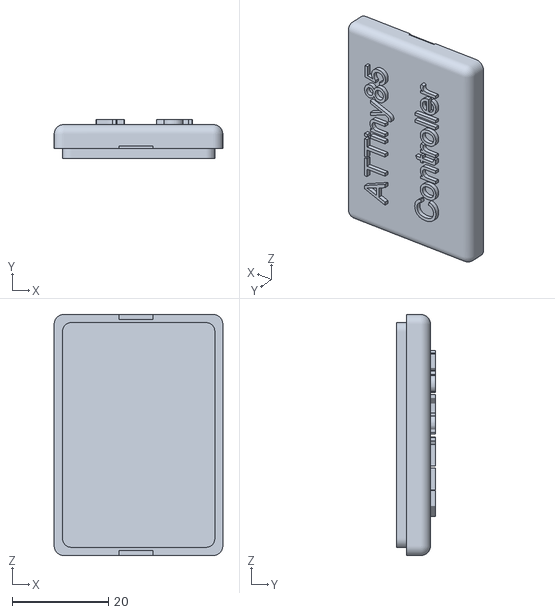
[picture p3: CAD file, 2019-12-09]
Additional_File_18_Skimmer_control_box_lid.stl
35.0 x 8.00 x 50.0

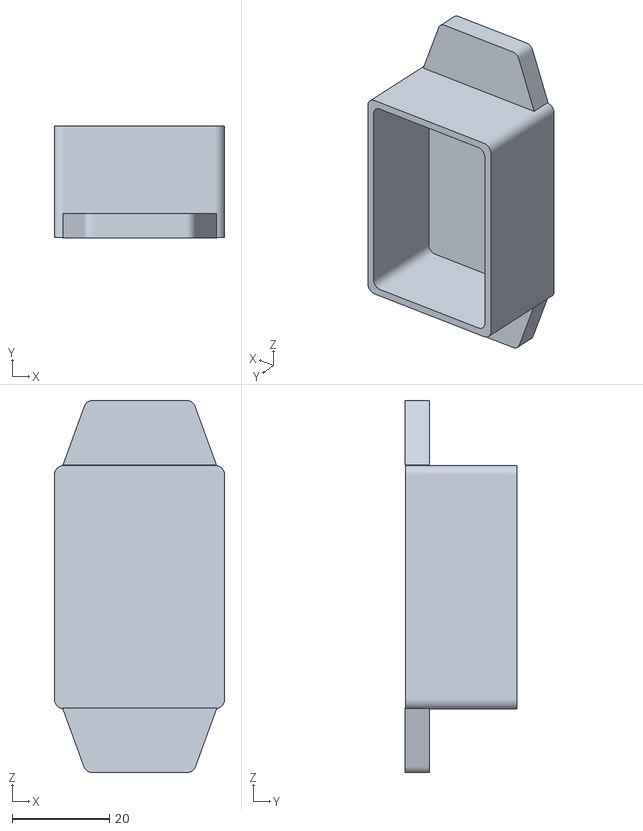
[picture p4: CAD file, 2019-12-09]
Additional_File_17_Skimmer_control_box_housing.stl
35.0 x 23.1 x 76.4

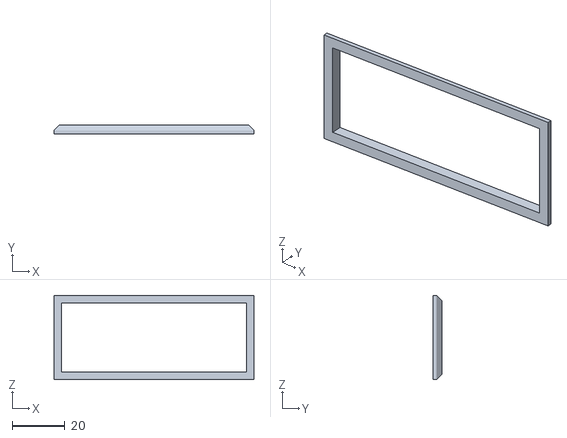
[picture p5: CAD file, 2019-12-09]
Additional_File_6_LCD_Bezel_98.stl
75.9 x 3.23 x 31.9

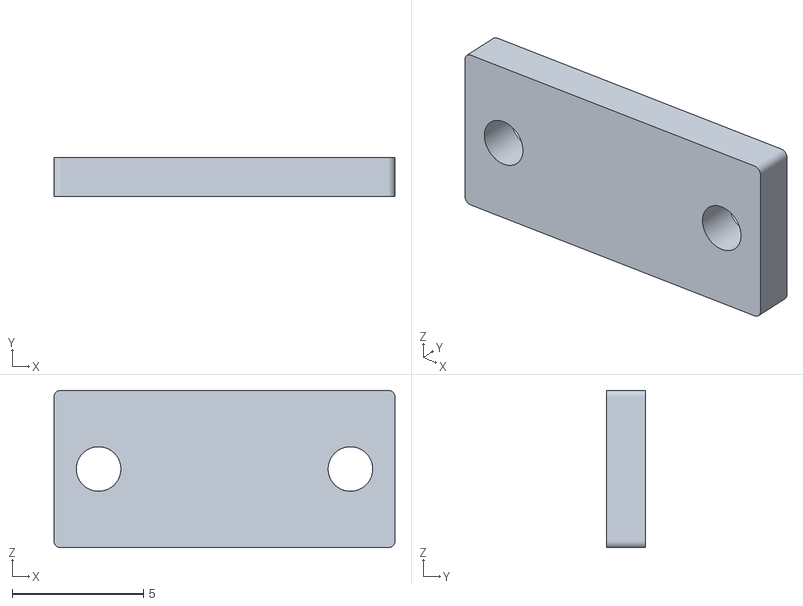
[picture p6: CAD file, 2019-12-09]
Additional_File_12_IR_sensor_retaining_strap.stl
13.0 x 1.50 x 6.00

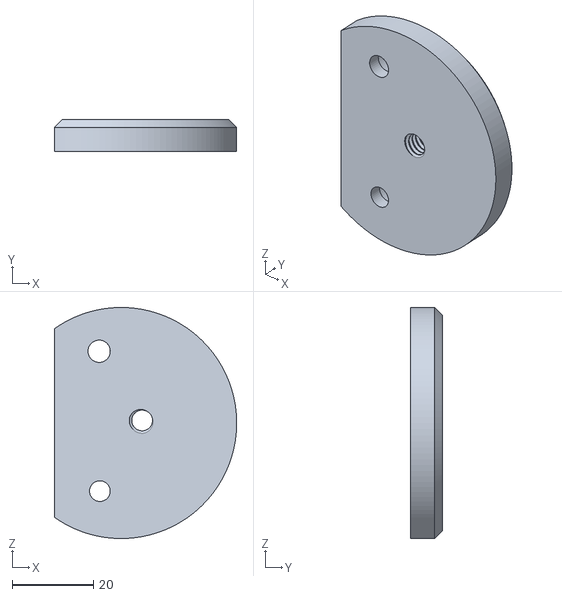
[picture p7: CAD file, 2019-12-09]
Additional_File_8_Articulated_arm_base_plate_2.stl
45.0 x 8.00 x 57.0

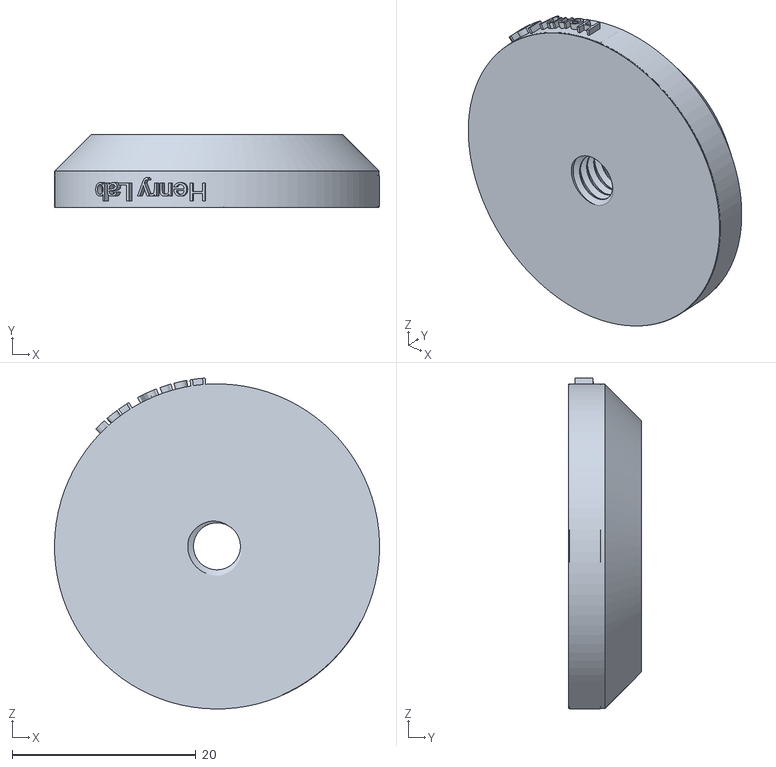
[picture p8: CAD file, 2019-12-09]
Additional_File_7_Articulated_arm_base_plate_1.stl
35.4 x 8.00 x 36.0

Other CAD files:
Additional_File_11_IR_LED_retaining_strap.stl

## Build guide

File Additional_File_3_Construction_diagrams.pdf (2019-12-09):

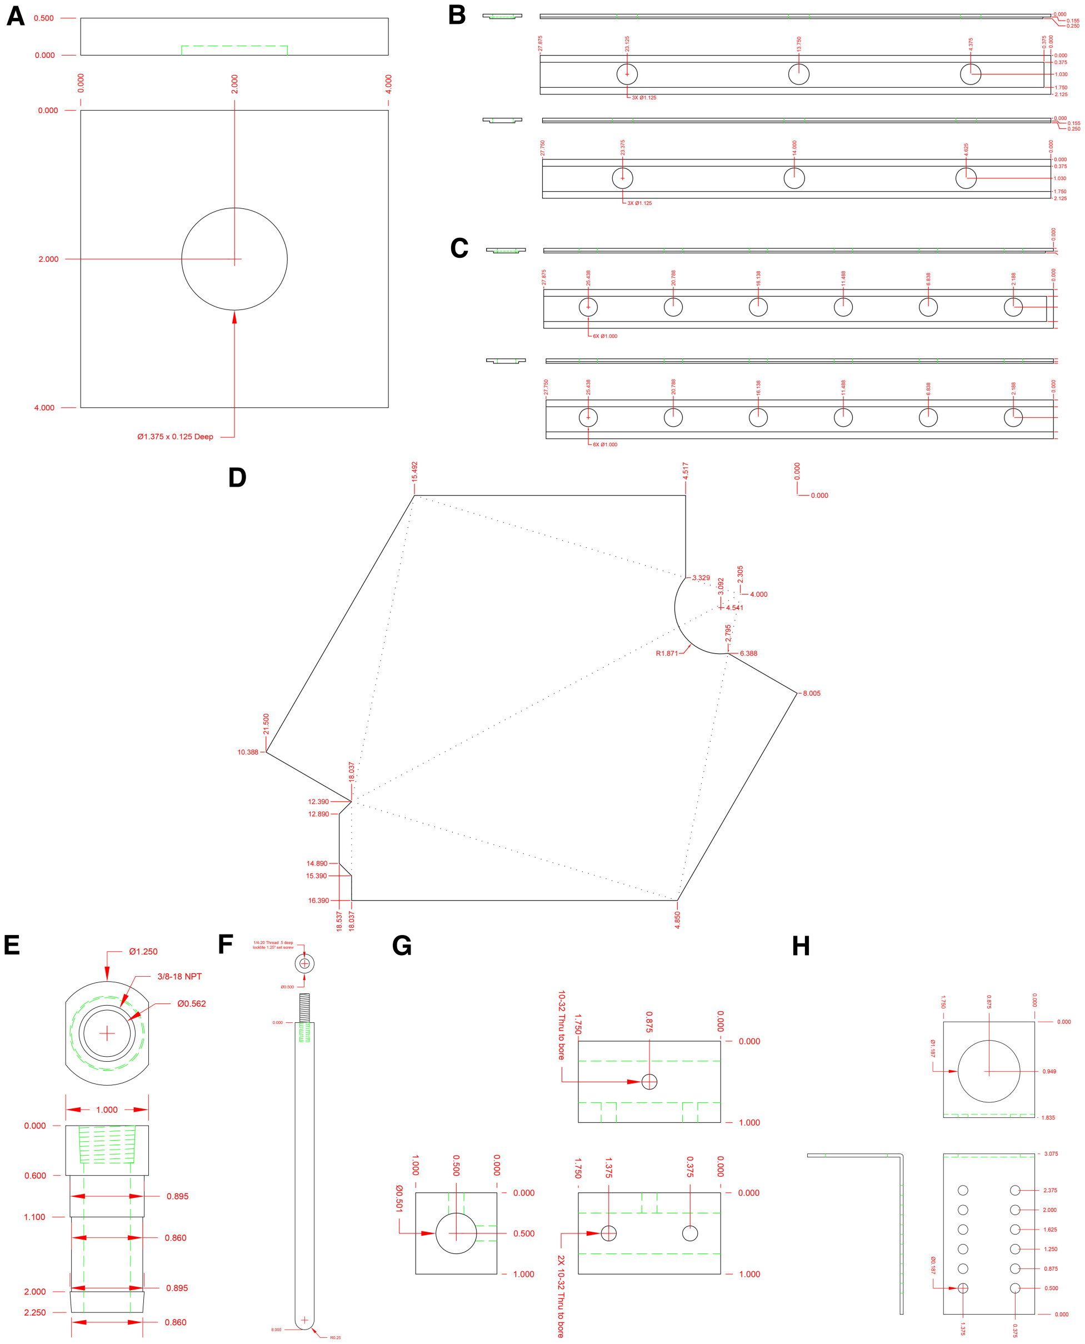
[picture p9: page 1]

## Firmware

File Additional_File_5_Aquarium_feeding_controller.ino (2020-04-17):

//This sketch is for the feeding system that delivers liquid food to the automated marine aquatic system.  This is a final, revised working version.
//A change was made since the previous version to restrict the air purge cycle, which avoids a condition in which the program could get stuck
//waiting for the food to leave the line shoul it becomes clogged. This unfortunate event could prolong the feeding bypass condition in the rack system,
//which could possibly go on indefinitely. A change was also made to move the stir cycle out of the feeding loop and only have it mix at 5 min before the 
//hour.  Currently the timing of feedings is set to once every two hours for 24 mins. In addition, the time for pumping is set to 30 secs which is enough 
//for the pump to complete its cycle.  This may need to be changed for larger volumes. Also once a low food alert is sent, this triggers the warning LED
//warning light to turn RED, but if the sensor no longer sees a low level the red status light will remain lit until the next feeding cycle begins or ends,
//or is reset at 55 mins past the hour for a stir cylce. Also, I have added a way to check that food entered the line, and if not, it sends a text, and to
//send a text if food never leaves the line. Possible future improvements include some way to continue showing the red fault LED once the next
//feeding cycle starts or stops (now if will change to blue or green momentarily until the sensor again detects the low food level).

//Uses date and time functions from a DS1307 RTC connected via I2C, with a battery backup. The program controls feeding cycles of the automated aquarium
//system for Crepidula snails (controls the aquarium bypass valve, stir plate, peristaltic pump and air pump). Stir plate and aquarium pump are controlled
//via relays for 120 volts AC in the remote outlet box. The controller also monitors food levels in the reservoir using an NPN capacitance sensor, and 
//sends a text message if there is a problem (e.g., food supply is Low). The script also incorporates an alarm test to avoid rapidly resending low food text
//alerts. The alarm status is reset only at 55 mins past the hour so texts should only be repeated once an hour. System, also monitors food passage through
//the feeding tube using a 38KHz pulsed IR LED and sensor. The Ethernet sheild uses pins 10 (used to deselect W5100 to disable it, set as output and set HIGH,
//but we are using it so no need to do that here), 11, 12, 13, as well as pin 4, which is used two deselect SD card, set as output and set to HIGH, which is
//needed here, as we are not using the SD card). (Thus, we have Ethernet W5100 enabled and disable the SD card). If using W5200 or later version, one would
//need a different, updated ethernet library. Below we also use pins 2, 3, 5, 6, 7, 8, 9. Analog pins A4 and A5 are used for the RTC for the I2C SDA and SCL
//pins Analog pins A0, A1, and A2 are used to control the power switch's three LEDs (Green, Blue, Red) to show system status alerts. Also incorporates alarm 
//test to avoid resending low food text alerts. Define them as OUTPUT pins, setting them to ground each LED to light them To write to the LCD display we 
//currently use the TX pin 1, but this creates problems if one uploads code while display is connected. This can corrupt the display's eprom settings requiring
//that it be reset using Afrtuit's LCD script. It would be better to use Software Serial and redefine the TX pin (to analog pin A3, as it is the only other
//available, free pin). First created by J. Henry on July 30, 2018, continuously updated until April 16, 2020. This project was funded by an NSF EDGE grant
//(no. 1827533) to J.J. Henry.

#include "Arduino.h"
#include <SPI.h>
#include <RTClib.h>//Realtime clock library
//#include <EthernetV2_0.h>//needed to run the ethernet shield, V2 for W5200 chip, note thisa needs to be set that up inside the library
#include <Ethernet.h>//needed to run the ethernet shield, needed for W5100 chip
#include <Wire.h>// also included here as the RTClib depends on it
#include <LiquidCrystal.h>//needed for LCD display
//#include <SoftwareSerial.h>//needed only if one wants toi redefine the rx and tx serial pins to run the lcd display


#include <IRremote.h>

#define PIN_IR 3//38khz pulsed output pin for IR LED
#define PIN_DETECT 7//detection pin for IR sensor

// Create a software serial port!
//SoftwareSerial lcd = SoftwareSerial(0,A3);//RX, TX: use this only to create a new tx pin for LCD

RTC_DS1307 rtc;
//IR sensor is on the tank feeding line and is attached to Pin 3
//note NPN will source a negative, whle PNP will source a positive signal. So if using an NPN sensor
//the sensor will go LOW when it senses liquid, so use pull up resistor on these pins
#define supplyPin 2//capacitance liquid sensor output monitors the food supply line and is attached to Pin 2

int checksum = 1;//begin as a non-feeding cycle = 1
int alarm = 0;
int count = 0;//part of air pump alert

//ethernet setup
byte mac[] = { XX, XX, XX, XX, XX, XX };// user definable, unique mac address for this device need to change this!! Check with your IT department.
// change following network settings to yours
IPAddress ip( ##, ##, ##, ## );       // unique IP address for this device, need to change this!!
IPAddress gateway( ##, ##, ##, ## );    // change to internet access via router, not always needed, unique address, need to change this!!
IPAddress subnet( ##, ##, ##, ## );    // change to subnet mask, not always needed, unique address, need to change this!!
IPAddress myserver( ##, ##, ##, ## );   // for email alarm, unique address device, need to change this!!
//EthernetServer server(8080);           // server port : remember to set port forwarding on the DSL router, if needed, we don't need this for this sketch
EthernetClient client;

IRsend irsend;
void setup()
{

  pinMode(PIN_DETECT, INPUT);// make this pin an input pin
  irsend.enableIROut(38);//pulses IR LED at 38Khz, for selectivity IR sensor can only detect IR light at 38K hz
  irsend.mark(0);//

  pinMode(A0, OUTPUT);//redefine analog pin as output to control system status LED, nominal, green
  digitalWrite(A0, LOW);//set the pin to LOW, negative TO TURN ON THE GREEN LED
  pinMode(A1, OUTPUT);//redefine analog pin as output to control status LERD, feeding, blue
  digitalWrite(A1, HIGH);//set the pin to HIGH, positive, TO TURTN OFF THE BLUE LED
  pinMode(A2, OUTPUT);//redefine analog pin as output to control system status LED, alert, red
  digitalWrite(A2, HIGH);//set the pin to HIGH, positive, TO TURN OFF THE RED LED
  pinMode(A3, OUTPUT);//redefine analog pin as output to control system status LEDs as a positive +5VDC source
  digitalWrite(A3, HIGH);//set the pin to HIGH, positive, +5VDC source
  //note that analogs pins A4 and A5 are used for the I2C SDA and SCL pins, respectively and no need to define these here
  pinMode(2, INPUT);//from capacitance sensor
  digitalWrite (2, LOW);// For OPNO sensor; Reverse if using NPN sensor (HIGH) to activate pullup resistor.
  pinMode(5, OUTPUT);//to relay board, relay coil is not energized when input is HIGH
  digitalWrite(5, HIGH);
  pinMode(6, OUTPUT);//to relay board, relay coil is not energized when input is HIGH
  digitalWrite(6, HIGH);
  pinMode(8, OUTPUT);//ttl output for aquarium system bypass valve
  digitalWrite(8, LOW);
  pinMode(9, OUTPUT);//ttl output for syringe pump
  digitalWrite(9, LOW);
  //while (!Serial); // use for Leonardo/Micro/Zero, here we use Uno

  Serial.begin(9600); //baud rate for communications
  pinMode(4, OUTPUT); // needed for the ethernet sheild to inactivate the SD card
  digitalWrite(4, HIGH);//inactivate the SD card
  Ethernet.begin(mac, ip, gateway, gateway, subnet);
  delay(2000);


  if (! rtc.begin()) {
    Serial.println("Can't find RTC");
    while (1);


  }

  if (! rtc.isrunning()) {
    Serial.println("RTC not running");
    delay(1000);
    //This next line sets the RTC with an explicit date & time, for example to set January 21, 2014 at 3am you would call:
    //rtc.adjust(DateTime(2014, 1, 21, 3, 0, 0));// nly need to implement this once or for a DST change
    //The following line sets the RTC to the date & time of the computer, only needed once or for a DST change
    //rtc.adjust(DateTime(F(__DATE__), F(__TIME__)));//This phrase uses computer time to set the RTC. But note a bug can't get time to reset on my new Mac!?

  }

}

void loop () {//the main loop

  //Serial.write(0xFE);//turn off Adafruit serial lcd display backlight, but here we leave it on
  //Serial.write(0x46);
  //delay(10);
  //also not sure we need this next bit, so will inactivate it, I believe this is in eprom, non-volatile memory
  //Serial.write(0xFE);//turn autoscroll on, new text will appear on first line only
  //Serial.write(0x51);
  //delay(10);

  DateTime now = rtc.now();//queries the RTC
  delay(1000);
  //now let's print out the current set date and time, Only using time here
  //Serial.print(now.year(), DEC);
  //Serial.print('/');
  //Serial.print(now.month(), DEC);
  //Serial.print('/');
  //Serial.print(now.day(), DEC);
  //Serial.print(' ');
  Serial.print("Time");
  Serial.print(' ');
  Serial.print(now.hour(), DEC);
  Serial.print(':');
  Serial.print(now.minute(), DEC);
  Serial.print(':');
  Serial.print(now.second(), DEC);
  Serial.println();
  delay(1500);

  //lcd.write(0xFE);//more settings for the LCD, not needed here
  //lcd.write(0x58);
  //delay(10);
  {
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

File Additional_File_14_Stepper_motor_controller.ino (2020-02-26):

//Peristaltic Pump Controller. This sketch works nicely.
//This fully working code uses a joystick to increment or decrement 2 values to be stored in eeprom memory
//This sketch has been combined with the peristalitic pump program.
//THius sketch no longer incorporates an interrupt on digital pin 2 (Interrupt 0) to recieve the signal from the feeding 
//station microcontroller to activate a feeding via the peristalitic pump. Note that the interrupt pin 
//input is suseptable to static electricity or RF and may be triggered as such. Better sheilding may be required.
//Some pull-down resistor values needed to be changed.
//To work without interrupts I lengthened the time of the HIGH trigger pulse from 200msec to 400msec in the feeding controller 
//sketch, to be sure this loop here catches it. One could add a forward, primming/purge momentary button. This could be 
//simply donw by supplying Vcc +5VDC to the input Pin 2. If you hold the button down (HIGH) it should continue to pump. 
//For now one has to manually use a wire jumper between the input pin 2 (also pin 2 on the DB9 connector) and Vcc +5VDC, which is
//being carried by pin 1 of the DB9 connector. Note that ground is carried on pin 9 of the DB9 connector.
//Sketch by Dr. J.J. Henry, UIUC, 12/3/2019.

#include <EEPROM.h>
#include <Stepper.h>

//int counter1 = 0;
byte setting1 = 0;//a variable which holds the speed value we set, is a byte for values up to 255
byte setting2 = 0;//a variable which holds the steps value we set, is a byte for values up to 255
//const int ledPin =  13;//the number of the LED pin as a diagnostic readout for the feeding cycle and used to put DRV8833 to sleep
//volatile int buttonState = 0;//variable for reading the pushbutton status
//const byte interruptPin = 2;//input from feeding station to trigger a feeding, used as an interrupt pin

const int  stepsPerRevolution = 200;//change this to fit the number of steps per complete revolution for your stepper motor
//currently we use 1.8 degrees per step

// initialize the stepper library for pins 8 through 11:
Stepper myStepper(stepsPerRevolution, 8, 9, 10, 11);

void setup() {
pinMode(7, INPUT_PULLUP); //input for storing stepper motor values permanently to eeprom memories = "sel" pin
//on adafruit joystick the push button is normally closed (1) and shorts to ground (0) when pressed.
pinMode(13, OUTPUT);//initialize the LED on pin 13 as an output:
digitalWrite(13, LOW);
pinMode(2, INPUT);//initialize the pin as an input
//digitalWrite(2, LOW);//start with this pin LOW to turn off pull up resistor
//attachInterrupt(digitalPinToInterrupt(interruptPin), pin_ISR, RISING);//Attach an interrupt to the ISR vector, and one cannot use "HIGH" on uno
setting1 = EEPROM.read(1);//recall stored value for speed (rpms)
setting2 = EEPROM.read(2);//recall stored value for steps, to deliver a specific volume, which needs to be calibrated in advance
//here one complete revolution is 180 ul with 4mm OD and 2mm ID silicone tubing

Serial.begin(9600); //baud rate for communications
delay(50);
//present the current settings on the LCD:
Serial.print (setting1);
  Serial.print ("RPM / ");//speed
  delay(400);
Serial.print (setting2*50);//multiply Byte value times 50 as each step is only 0.9ul
//this means that currently with a max byte value of 255 we can only deliver 12750 steps or 63.75 revolutions or 11.48ml
//one byte adds 0.45ul
//Note that we could add a calculation to figure out the actual volume instead and print this volume
  Serial.println ("ST");//"steps"
  delay(400);
}
void loop() {
 
  digitalWrite(13, LOW);//illuminate the LED when the interupt pin is HIGH, each time you run through the loop drive this pin LOW
  //to put the DRV8833 to sleep
 delay(50);
 
 if (digitalRead (2) == HIGH){//check to see if there is an input from the feeding controller to trigger the pump
 //Serial.println(buttonState);
 digitalWrite(13, HIGH);//shows that the pump is active and is needed to provide power to slp pin on the DVR8833 stepper motor Driver board
//NOTE! use this pin 13 to also activate the stepper motor driver board (DVR8833, connect it to the "slp" pin, which must be high to provide power to the motor)
 //In this way the motor will not get hot when it is idle. By default the slp pin is pulled low = inactive, and see code above

  //speed is set as rpm
setting1 = EEPROM.read(1);//recall stored value for speed (rpm)
  //or 1/42 revolution minimum
setting2 = EEPROM.read(2);//recall stored value for steps, to deliver a specific volume, which needs to be calibrated in advance
 Serial.println ("Feeding");
 myStepper.setSpeed(setting1);//set equal to rpms in memory, as a byte
    delay(200);
 myStepper.step(setting2*50);//deliver the food set to steps in memory, as a Byte value times 50
 //note that the pump will complete its pumping cycle before returning back here to the main loop
    delay(20);
    Serial.println ("Done");
    digitalWrite(13, LOW);//put the DRV8833 back to sleep

delay(1500);//wait long enough so as not to trigger another pumping, one may not really need this long delay, as pumping is long enough

//buttonState = 0;//reset the button state for the next feeding

//present the current settings on the LCD:
Serial.print (setting1);
  Serial.print ("RPM / ");
  //delay(400);
Serial.print (setting2*50);//multiply Byte value times 50
  Serial.println ("ST");
  delay(500);

 }
 
  
int sensorReading1 = analogRead(A0);
int sensorReading2 = analogRead(A1);
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

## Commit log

2019-12-09 Automated Feeding Controller
    [Supplemental_File_9_tubing_holder_base.stl]
2019-12-09 new changes
    [Supplemental File_16_Skimmer_control_box_lid.stl, Supplemental_File_10_tubing_holder_top.stl, Supplemental_File_6_LCD_Bezel_98.stl]
2019-12-09 name changes
    [Supplemental_File_11_IR_LED_retaining_strap.stl, Supplemental_File_12_IR_sensor_retaining_strap.stl, Supplemental_File_15_Skimmer_control_box_housing.stl]
2019-12-09 name chnages
    [Supplemental_File_13_DC_motor_controller_interface2.fzz, Supplemental_File_4_Feeding controller2.fzz, Supplemental_File_7_Articulated_arm_base_plate_1.stl]
2019-12-09 name change
    [Supplemental_File_16_Skimmer_control_box_lid.stl]
2019-12-11 name changed
    name changed
    [Supplemental_File_13_DC_motor_controller_interface22.fzz, Supplemental_File_7_Articulated_arm_base_plate_11.stl, Supplemental_File_9_tubing_holder_base22.stl]
2020-02-26 name changes and updates
    [Supplemental_File_13_Peristaltic pump controller.fzz, Supplemental_File_4_Feeding controller2.fzz, Supplemental_File_4_Feeding_controller2.fzz]
2020-03-16 File name changes
    [Additional_File_18_Skimmer_control_box_lid.stl]
